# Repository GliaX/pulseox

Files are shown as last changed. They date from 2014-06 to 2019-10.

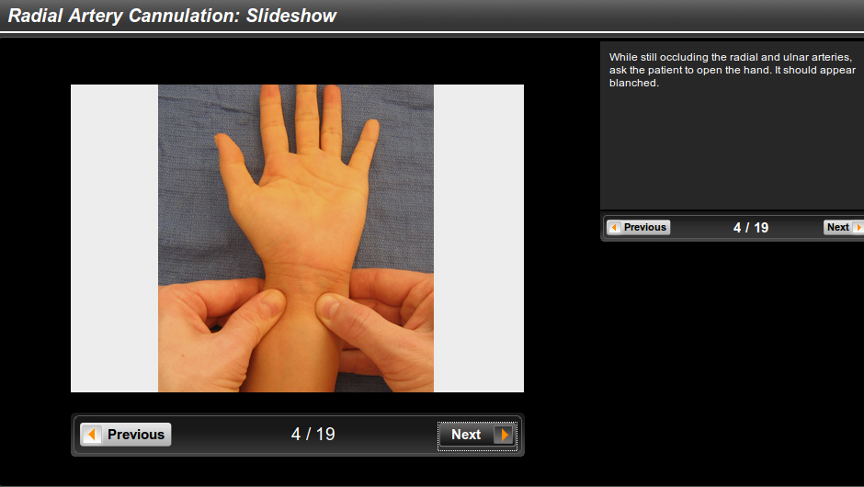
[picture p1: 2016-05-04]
ethics_application/radial_cannulation/radial_explainer_04.png

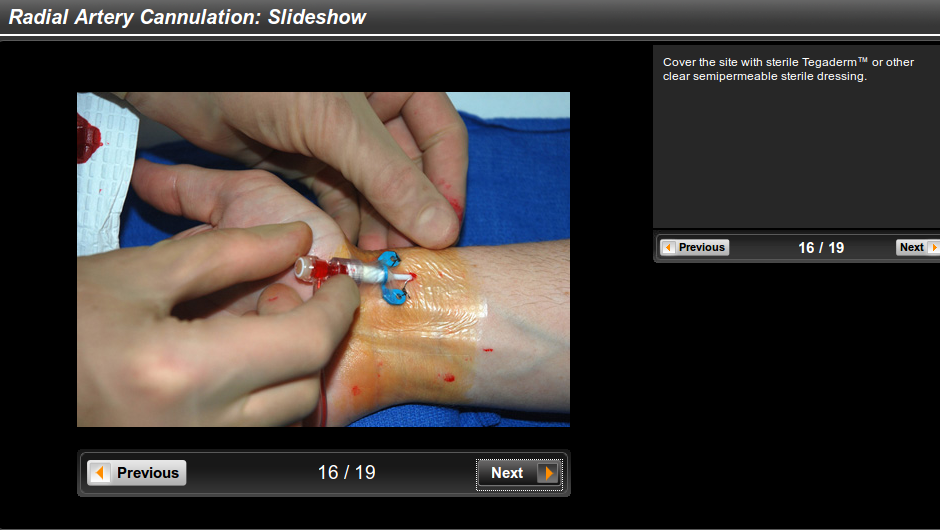
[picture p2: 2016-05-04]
ethics_application/radial_cannulation/radial_explainer_16.png

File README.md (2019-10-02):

Pulse Oximeter
==============

This project aims to create a research-validated pulse oximeter whose plans are available freely and openly. The goal is for the device to cost under USD$25 to produce.

Currently, **THE PULSE OXIMETER IS NOT USABLE AND SHOULD NOT BE USED IN A CLINICAL SETTING.** The current version can be used for laboratory testing only.

Status
======
The device is undergoing clinical calibration as of 2019 OCTOBER 2.

Installation
============
Clone the repository and then do the following to initialize the submodules:

```
git submodule init
git submodule update
```

Licensing notes
===============
As per our understanding, hardware is not covered by copyright. However, we present
our work under the TAPR OHL license insofar as it applies. All software is covered by the GNU aGPL V3

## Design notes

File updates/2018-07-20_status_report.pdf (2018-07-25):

## GliaX Status Report

Progress report since Mon 9. 7. 2018 up to Fri 20. 7. 2018.

PULSE OXIMETER

Features added:
1. finger presence detection implementation
2. automatic LED brightness adjustment algorithm implemented

### 1. FINGER PRESENCE DETECTION

Finger presence algorithm serves both as a user experience feature as well as trigger for other actions, loops and processes that happen in firmware. It takes the level of raw_red signal as a reference to detect the finger presence. As soon as detected level falls below the specified threshold, that means the finger was inserted and device calibration is initialized. Before that, the device is at standby and “FINGER OUT” sign is seen on the display. If the finger is removed during measurement, the device displays the same sign however the brightness level remains the same once the finger is re-inserted and the measurement reappears in a few seconds again.

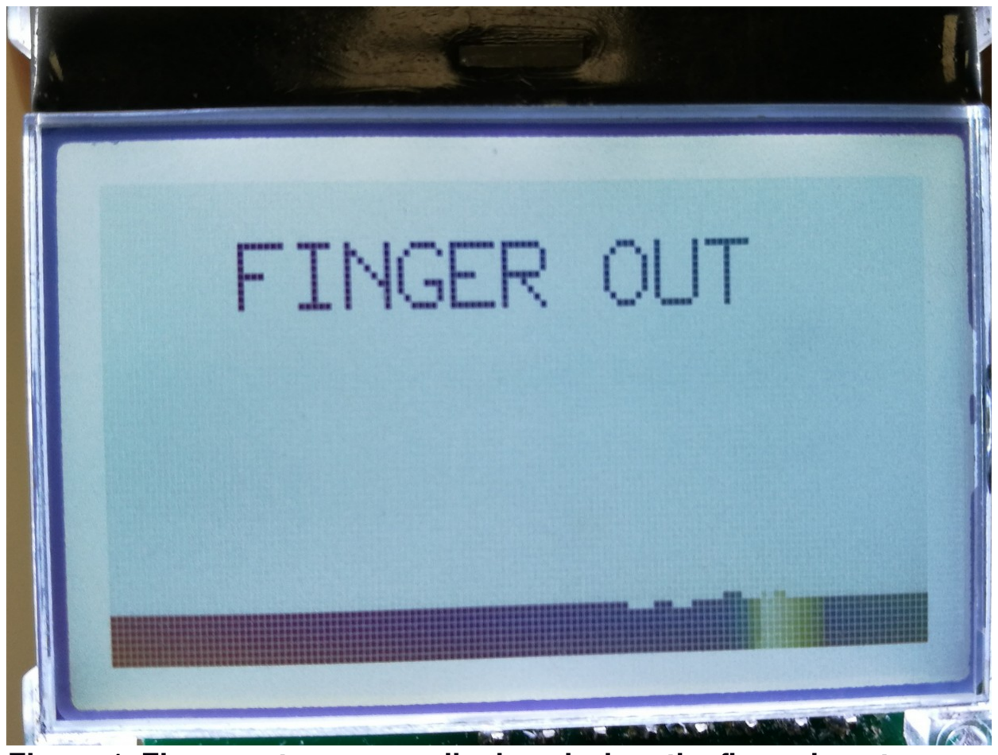
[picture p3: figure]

Figure 1: Finger out message displayed when the finger is not present.

### 2. AUTOMATIC LED BRIGHTNESS ADJUSTMENT ALGORITHM

Device Calibration

Automatic LED brightness algorithm is necessary to compensate for finger light absorption. Light absorption at different wavelengths varies with skin thickness, pigmentation etc. of the person therefore each specimen will have a different optimal light intensity necessary to have the finger illuminated at the right intensity to get the optimal reading.

The calibration process is divided up into setup loop and test loop. The setup loop is initiated right after the finger presence is detected. When pulse is detected, a test loop is initiated which runs the fine optimization. The user sees a message “CALIBRATING...” displayed on the screen¹
until brightness
levels of IR and RED LEDs are successfully adjusted. Afterwards, the device switches to normal operational mode.

1 NOTE: The function for message display is already implemented in the firmware but is not yet turned on due to chip memory issues. The code will first be optimized to increase available ROM, then the function will be enabled. Visually it is similar to what is shown in the Figure Figure.

### 2.1 SETUP LOOP

Setup loop is initiated upon the presence of the finger. It begins at initial brightness level²
and changes it
stepwise until pulse is detected. Brightness level change is executed in a fixed time window of 3 seconds, ensuring enough time for detection of at least 2 heart beats when brightness is close to satisfactory level. Once heart beat is detected, the setup loop is terminated and test loop starts instantaneously. This change is still unseen to the user.

2 NOTE: The initial brightness levels need to be tested locally to achieve the time-optimized solution. The current solution will work best with light-skinned people, but could take a little more time to settle when used on a patient with more pigment.

### 2.2 TEST LOOP

The test loop starts as soon as heart beat is detected and is there to achieve the best signal-to-noise ratio after we already have a useful signal. It is based upon an invented variable that describes ratio between noise and useful signal in the measurement. The variable is named Signal Quality Index (SQI) and is calculated as

SQI = 1 STD/AMP – | (1)

where STD is the signal standard deviation of the signal noise and AMP is signal amplitude when noise is filtered out (see Block diagram in the Figure 2).

Upon successful stabilization of IR and RED brightness levels, the device switches into normal operating mode. At this point the best possible signal quality is achieved.

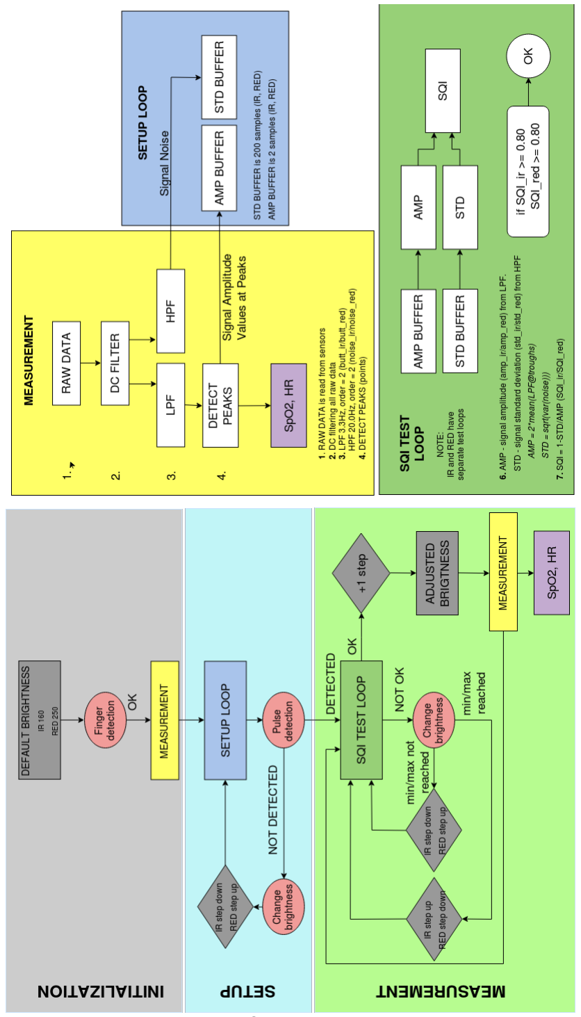
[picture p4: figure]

Figure 2: Code block diagram.

Safety Measures

AVOIDING CONTINUOUS CALCULATIONS
To avoid continuous calculations, we first check for presence of finger in the sensor, and only then brightness adjustment function starts. Brightness adjustment is happening in predefined steps (which can be adjusted) between max and min possible value (also predefined). To make sure the process takes the least possible time, we change brightness in both directions, up and down. This way we ensure that we reach optimal brightness as soon as possible.

REMOVAL OF FALSE-POSITIVES IN PEAK DETECTION
When detecting a pulse from signal peaks, we need to avoid detecting false positives. For that purpose a threshold value was empirically derived and introduced as a safety parameter.

BUFFER MANAGEMENT
When calculating SQI values we need to ensure that all data used is time-aligned. This is done by emptying all used buffers after each test loop iteration. The test loop runs on IR and RED signal completely separately.

VALUE THRESHOLDS
Signal minimum and maximum threshold values were introduced ensuring that too noisy or too weak signals are ignored.

Next Steps

- retesting of the automatic brightness adjustment algorithm
- Finalization of project documentation
- Release debug version of firmware to Tarek Loubani for testing

To be completed by: 27. 7. 2018

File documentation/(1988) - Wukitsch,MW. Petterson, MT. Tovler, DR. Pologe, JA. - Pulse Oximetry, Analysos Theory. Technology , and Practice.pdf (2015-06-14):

# Knowing Your Monitoring Equipment

PULSE OXIMETRY: ANALYSIS OF THEORY,

## TECHNOLO6Y, AND PRACTICE

Michael W. Wukitsch, BA,
Michael T. Petterson, BA, RRT, CPFT, David R. Tobler, BSEE,

### and Jonas A. Pologe, BSEE

Wukitsch MW, Petterson MT, Tobler DR, Pologe JA. Pulse oximetry: analysis of theory, technology, and practice.
J Clin Monit 1988;4:290-301 ABSTRACT, Interest in two-wavelength classic, that is, nonpulse, oximetry began early in the 20th century. Noninvasive in vivo measurements of oxygen saturation showed promise, but the methods were beset by several problems. The pulse oximetry technique, by focusing on the pulsatile arterial component, neatly circumvented many of the problems of the classic nonpulse arterial approach. Today's pulse oximeter owes a good measure of its success to the technologic advances in light emission and detection and the ready availability of microcomputers and their software. Many clinicians have recognized how valuable the assessment of the patient's oxygenation in real time can be. This appreciation has propelled the use of pulse oximeters into many clinical fields, as well as nonclinical fields such as sports training and aviation. Understanding how and what pulse oximetry measures, how pulse oximetry data compare with data derived from laboratory analysis, and how the pulse oximeter responds to dyshemoglobins, dyes, and other interfering conditions must be understood for the correct application and interpretation of this revolutionary monitor.
KEY WORDS. Measurement techniques: pulse oximetry. Monitoring: oxygen. Equipment: pulse oximeters.

THE THEORY

From Ohmeda, 1315 W Century Dr, Louisville, CO 80027. Address correspondence to Mr Petterson.

I placed my prism at this [light] entrance, that it might be refracted to the opposite wall. It was at first a pleasing divertissement to view the vivid and intense cotours produced thereby... [Sir Isaac Newton (1642 to 1727), in a report in the Philosophical Transactions for 1672]

Light was, therefore, recognized to contain all colors of the visible spectrum of electromagnetic energy. Measurements of electromagnetic vibrations are frequency, expressed in hertz (Hz) (1 Hz = one cycle per second) and wavelength, expressed in nanometers (nm) (1 nm = one thousand millionth [1 x 10 -9] of 1 m). Red light, as used in PuLs~ OXIMETRY, can be measured at a frequency of 4.3 x 1014 Hz or a wavelength of 660 nm. The nanometer, yielding numbers much easier to deal with, is the unit typically used when discussing this part of the spectrum.
Newton's theory fostered the techniques of spectral analysis--that is, the ability to detect elemental composition by defining the unique light absorption "fingerprints." A major theoretic statement in early laboratory spectral analysis was the Beer-Lambert (or Bouguet's) law. Simply, this law states that the concentration of absorbant in solution can be determined as a mathematical function of the amount of light transmitted through the solution, providing that the intensity of incident light, the path length, and the ~XTINCTION CO-

290 Copyright © 1988 by Little, Brown and Company

Monitoring Equipment: Wukitsch et ah Pulse Oximetry 291

,=,
I eeOnm

o

X
LtJ

-2
6oc

(l~=~,=mo)
94Ohm
\
\ | \

Hb

I, | t, | I | t | ! | l
700 | | aoo | | aoo | looo
WAVELEENGTH (nm)

Fig 1. Oxyhemoglobin (HbO2) and reduced hemoglobin (Hb) exhibit markedly different absorption (extinction) characteristics relative to red light at 660 nm and infrared light at 940 nm. (Courtesy of Ohmeda)

EFFICIENT of a substance at a particular wavelength are known. The absorbance of light by HEMOGLOBIN (Hb) and oxyhemoglobin (HbO2) as a function of wavelength is shown in Figure 1. The absorbance or, more correctly, extinction of HbO2 at the red wavelengths (650 to 750 nm) is less than that for Hb. Hence, HbO2 is more transparent to red light than Hb is. Figure 1 also shows that the reverse is true, to a lesser degree, in the infrared region (900 to 1,000 nm). Research led by Nicolai, Kramer, Elam, Matthes, Millikan, and Wood in the early to mid-1900s sought ways to apply these facts to determine the HbO2 concentration, or arterial blood oxygen saturation (SaO2) [1].
Complex and numerous problems of applying the Beer-Lambert law to in vivo analysis brought the development of two-wavelength, in vivo oximetry to a halt during the 1950s. Why the Beer-Lambert law was not totally effective becomes apparent when we examine how light behaves in this application.
As the law of conservation of energy states, energy cannot be "created or destroyed"--and this applies to light energy. For the Beer-Lambert law to work, all light in the system should be accounted for, that is, incident light = light transmitted + light absorbed. This can work in a very controlled experiment with relatively short path lengths. Experiments with human tissue present several obstacles. Consider: incident light = light transmitted + light absorbed + light scattered + light reflected. On human subjects:
- Light is scattered by the skin surface, tissue, muscle, bone, and blood.

* Light is reflected by the skin surface, which can be a function of skin surface texture and color.
- Light is absorbed by tissue components other than the blood and absorption is also dependent on pigmentation and thickness of the test site.
- The blood is a nonhomogeneous liquid capable of nonlinear absorption of light, particularly as hematocrit varies.

The CLASSIC OXIMETRY (that is, nonpulse, two-wavelength, in vivo oximetry) could not deal effectively with all the variables.

EVOLUTION OF PULSE OXIMETRY

The prominent forerunner to the pulse oximeter was the Hewlett-Packard ear oximeter (HP 47201A), which used a tour de force of technology to solve the problems found in the two-wavelength approach. By using eight wavelengths (from 650 to 1,050 nm), this unit compensated for all the effects of "skin pigmentation, ear thickness, or earprobe motion" [2]. Featuring precalibration, ear vascularization via heat, and a fixed path length, this unit solved many of the problems that plagued earlier devices [31.
Clinical accuracy tests pointed to the ear oximeter as an acceptable device that was a boon to the puImonologists and sleep researchers of the mid-1970s. Although it was thought to be the "gold standard" for oximeters, recent tests at low saturations uncovered unstable performance below an arterial oxygen saturation (SaO2) of 70%, and its inability to deal with carboxyhemoglobin (HbCO) is documented [4,5].
A major advance came with the recognition that the pulsatile nature of the arterial blood can be exploited in oximetry. Pulse oximetry uses the physiologic activity of the cardiac pulse as the basis for a system to determine SaO2. The idea of using the cardiac rhythm as a "filter" for in vivo measurement was first attempted in Japan. This new concept took commercial form in the Mochida Oximet (eventually Minolta), the first pulse oximeter manufactured and marketed. This unit relied on analog electrical circuitry and had bulky fiberoptic cables similar to those of the Hewlett-Packard ear oximeter. Its performance was nearly acceptable clinically, with marginal accuracy, "_+ 5% of that obtained from the blood gas method" [6], and it exhibited some problems with artifacts: "The measurement is interrupted when the fingertip changes its position against the light beam. This frequently occurs when the patient is shivering" [6]. As with classic oximetry, early pulse oximetry had to contend with limitations inherent in the hardware.

292 Journal of Clinical Monitoring Vol 4 No 4 October 1988

10

0

0
o
c-O
0 .1

×
ILl

.01
600
Log~
~ | methemoglobin

~ogtobm

carboxyhemoglobin
I | I | I | I | I | 1 | ~ | | I | I
640 | 680 | 720 | 760 | 800 | 840 | 880 | 920 | 960 | 1000
Wavelength (nm)

Fig 2. Hemoglobin extinction curves showing relationship of reduced hemoglobin, oxyhemoglobin, carboxyhemoglobin, and methemoglobin to light absorption. (Courtesy of Ohmeda)

The first successful new-breed pulse oximeter, the Biox II (Ohmeda), ushered in a new era. The Biox II was a microprocessor-based, convenient-to-use, smaller, and less expensive device having clinically acceptable accuracy [7, 8]. Major interest in pulse oximetry in the United States was sparked by the efforts of Dr William New (Nellcor), who saw the advantage of oxygenation monitoring during anesthesia. Optimizing one of the key elements of this new approach--small, inexpensive light emitters and detectors--the Nellcor N100 featured disposable sensors.

PULSE OXlMETRY: PRINCIPLES

In order for spectrophotometric measurements of blood to be made in vivo a number of criteria must be met:

1. The tissue must be reasonably transparent to the wavelengths of light that are to be considered for the measurement.
2. The absorption characteristics must be different between the specific species for each wavelength that is to be considered.
3. There must be a reasonable method for producing the wavelengths that are being considered.
4. There must be an acceptable means of detecting the wavelengths of interest.
5. The minimum number of discrete wavelengths that are required must be equal to the number of significant absorbers that are present.

The first criterion limits the range of wavelengths that are reasonable choices to the red and near-infrared regions. Tissue and pigmentation absorb the blues, greens, and yellows, and water absorbs the longer infrared wavelength. As can be seen in Figure 1, Hb and HbO2 vary substantially relative to each other in the 600- to 1,000-nm range (red to near inffared)--this meets the second criterion. The availability of light sources in this region is quite good. There are a variety of light-emitting diodes (LEDs) with outputs in this wavelength region; they are commonly used for displays and optical communication applications. In addition, they are small, efficient, and reasonably stable. Two common LEDs have nominal wavelengths of 660 and 940 nm. The wavelengths in the range of 600 to 1,000 nm are also easy to detect v¢ith a silicon photodiode, thus fulfilling the fourth criterion. The last criterion is less straightforward. Obviously there are absorbers other than Hb and HbO2 in the blood. (Figure 2 shows the absorption characteristics of methemoglobin [MetHb], HbO2, reduced Hb, and HbCO.) Fortunately these four types of lib are the only significant absorbers normally found in blood. Note that at 660 nm, the MetHb and the Hb have similar extinctions (a measure of absorption), as do HbCO and HbO2. If only two

Monitoring Equipment: Wukitsch et al: Pulse Oximetry 293

TIME

Variable absorption due to pulseadded volume of arterial blood Absorption due to arterial blood Absorption due to venous blood

Absorption due to tissue

Fig 3. Tissue composite shows dynamic and static components affecting light absorption. (Courtesy of Ohmeda)

wavelengths are used the effect is, very roughly, to "lump" or combine MetHb with Hb and HbCO with HbO2.
The MetHb being seen as Hb usually is not clinically significant; because it is not carrying oxygen the oxygen saturation value is still correct. HbCO does present a problem because it will be "counted" as an oxygencarrying form and thus cause the measured oxygen saturation value to be reported larger than it actually is. The effects of these and other absorbers, such as dyes, are discussed later.
For a workable system, the signals coming from arterial blood must be isolated from those representing venous blood, tissue, and other absorbing material. The method by which this is accomplished is responsible for the termpulse oximetry. Figure 3 represents a tissue cross section. Note that light absorption by the various substances is constant over time, with the notable exception

Fig 4. Graphic representation of compensation process that must occur before light intensities at two wavelengths can be used for calculation of arterial oxygen saturation. This scaling process can be accomplished by several methods, electrically or mathematically,
AC = alternating current; DC = direct current; IR = infrared. (Courtesy of Ohmeda)

of arterial blood. The absorption signals from arterial blood vary with each contraction of the heart as the volume of arterial blood changes.
It is convenient to define the varying or dynamic part of the signal as the alternating current (AC) signal and the static component as the direct current (DC) signal. The amplitude of the DC signal is affected by the intensity of the light source, sensitivity of the detector, and amount of constant absorbers that are present (sample thickness). These same factors will affect the AC signal amplitude, as will the perfusion (amount of blood volume change per pulse) and the oxygen saturation. To make any useful comparisons between the absorption as the red wavelength and the infrared wavelength the AC signals must be scaled by the DC signals. Dividing the AC level by the DC level (at each wavelength) gives a corrected or scaled AC level that is no longer a function of the incident intensity [9].
This scaling process, performed by electronics, mathematics, or otherwise, yields values that are compensated for variations in incident light intensity and represent the relative absorption of light at two wavelengths that is due to only the hemoglobin in the arterial blood (see Fig 4). The numeric ratio of the corrected red value to that of the corrected infrared value yields a result that is easily converted to oxygen saturation, as shown in Figure 5. Figure 6 shows what the relative red and inflared AC signals would look like for various saturations.
The pulse oximeter's focus on just the "dynamic" arterial flow, along with the compensation process, neatly circumvent nearly all of the obstacles that have plagued the classic oximetry technique. Like all elegant solutions, pulse oximetry uses a simple concept to defeat complex problems. The simplicity, however, is deceptive.

AC--

~RAW ~ SIGNAL LEVELS
{WITH DC LEVELS UNEQUAL}

## Do ili ii ii!i!iiiiii'i' :ili iiiiiii

=SCALED ~ SIGNAL LEVELS
(WITH DC LEVELS EQUAL}

100
90
80
70
60
o ~ 50

40

30

20
10

0

Fig 5. Relationship of red (R)/infrared (IR) numeric ratio value to arterial oxygen saturation (SaO2).

PULSE OXlMETRY: PRACTICE

Converting the principles just described into a practical device for clinical application involves many additional considerations. These include technical issues related to optics, signal-to-noise ratios, data acquisition, signal processing, mechanical configuration, and human interface.
The oximeter probe consists of light sources (LEDs), a detector (photodiode), and an appropriate mounting structure to support the specific method of application. Electronically, the probe is quite simple in that the only necessary function is the ability to turn the LEDs on and off and to provide for the detected signal to be returned to the main electronics for processing. In addition, the probe provides a means of identifying itself to the system for calibration purposes. The mechanical structure today (owing much flexibility to the ideal light emitters and detectors that are available) is optimized on the basis of the intended application.
Electronically, the pulse oximeter consists of the following:
1. LED timing and probe control
2. Analog signal conditioning and/or processing
3. Data acquisition
4. Digital signal conditioning and/or processing
5. Display and control system
6. Internal system diagnostic functions

Three different light levels are measured by the detector: the red light level, the infrared light level, and the ambient light level. To accomplish this with a single detec-

O~

85~

100~

660nm (RED)

0 | 0 | 0 | 0 | 0 | 0 | 0 | 0 | 0 | 0 | 0 | 0 | 0 | 0 | 0 | 0
0 | C) | 0 | 0 | 0 | 0 | 0 | 0 | 0 | 0 | 0 | 0 | 0 | 0 | 0 | 0
6 6 6 ,.: ,; ,/. ,.: ,: ei gl 14 gl i4 ~4 ,,i ,4 8___
IR

940nm (IR)

/%_ ==3.4

1.0

- 43

Fig 6. Relative plethysmographic signal amplitudes and arterial oxygen saturation (SAG2) values assuming the transmission intensities are equal. R = red; IR ---- infrared.

Fig 7. Ohmeda light-emitting diode timing sequence shows frequency and first step of ambient light filtration process. R = red; IR = infrared; DC -- direct current. From Wukitsch MW. Pulse Oximetry: Historical Review and Ohmeda Functional Analysis. International Journal of Clinical Monitoring and Computing, Vol 4, pp 161-166, 1987. Used with permission.

tor the light sources must be sequenced on and off. Figure 7 shows the light timing sequence used in the Ohmeda 3700 oximeter. Each time the red LED is on, the analog electronics obtain a sample of the red intensity. This occurs likewise for the infrared LED. By measuring the light tevel when both LEDs are off, it is possible to subtract this level from each channel (red and infrared) on an instant-by-instant basis. This serves to compensate for ambient, or room, lighting, which may

Monitoring Equipment: Wukitsch et at: Pulse Oximet~ y 295

A

Fig 8. Representation of light-emitting diode sequencing occurring over 1/3o of 1 second as it relates to red (R)-infrared (IR) intensity sampling and the instantaneous arterial oxygen saturation (SaO2) calculation and the second step qsC ambient light filtering. To = time zero, or "'start"; T1 = time one, or "finish." From Wukitsch MW. Pulse Oximetry: Historical Review and Ohmeda Functional Analysis. International Journal of Clinical Monitoring and Computing, l/ol 4, pp 161-166, 1987. Used with permission.

change during the course of routine monitoring. Sequencing the LEDs at a frequency that is an integer multiple of the power line frequency allows the system to operate "synchronously" with "flickering" room lights (fluorescent lights normally generate a 120-Hz flicker on 60-Hz power). This avoids light flickerinduced fluctuations on the probe's photodetector, which could distort or disguise the tiny signals representing actual arterial blood flow'.
The light timing sequence, shown in Figure 7, cycles at 480 times per second (60-Hz power). A "stream" of these sequences, as depicted in Figure 8, shows the timing as it relates to the INSTANTANEOUS ARTERIAL OXYGEN
SATURATION (SaO2i) CALCULATION, which occurs thirty
times per second (60-Hz power):* It is significant that the 480-Hz timing, 60-Hz power, and 30-Hz SaO2i calculation are numerically related. The timing and sequencing frequencies serve as a filter against environmentally induced error [10].
Why SaO2i at 30 times per second? Since the pulse oximeter is making use ofpulsatile flow signal, the simplest approach might be to measure the minimum to maximum value (delta [A]) at the red and infrared wavelengths for each pulse and use this A red/A infrared value to calculate gaO 2 (Fig 9A). This method works but has a

*The light timing sequence and SaO2i calculation occur at 480 and 30 Hz, respectively, with 60-Hz power. With 50-Hz power, these numbers are 400 and 25 Hz, respectively.

B

Fig 9, Changes in light intensity can be measured at the minima and maxima points of the pulse wave or many times along the wave. X-X produces a change in intensities (A) on both red and infrared wavelengths. (A ) represents the change in light intensity from the minima to the maxima point on the arterial pressure wave form from which saturation can be calculated once per heart beat. The multiple measurements depicted in (]3) allow many sample points that can be subject to validation schemes such as the running weighted average. (Courtesy of Ohmeda)

number of unacceptable side effects. The first is that a calculation of oxygen saturation is possible only once per heart beat. Because some method of averaging the saturation values is required to minimize the effects of artifacts, and because there is a clinical requirement that the response time to changes in saturation be reasonably fast, one measurement per beat allows no more than ten measurements to be averaged for the system to maintain an acceptably short response time (10 s at 60 beats/ min). However, it is possible to make use of the principle that the sum of the parts equals the whole. By calculating the A, or change, in the signals 30 times per second, we can calculate the SaO2i value regardless of pulse rate (Fig 9B). With this method the Ohmeda pulse oximeter provides 180 saturation values in a 6-second interval (90 values in a 3-second interval). Having this large number of data points allows the use of a comprehensive scheme to selectively "weight" each sample to further enhance the stability of the calculation while maintaining acceptable responsiveness.

Table 1. Simplified Representation of Ten Sa02i Values with Assigned Weights
Variable | At One-Third of 1 Second
SaO2i (%) | 94 | 93 | 94 | 95 | 72 | 30 | 45 | 85 | 95 | 94
wti | 10 | 10 | 10 | 9 | 5 | 1 | 1 | 7 | 9 | 10
SaO2i x wti | 940 | 930 | 940 | 855 | 360 | 30 | 45 | 595 | 855 | 940

Table 2. Displayed Arterial Oxygen Saturation Values Derived from Averaging of Processed Average Values over Three Seconds
| Second 1 | | | Second 2 | | | Second 3
Processed average (avg v) | 92 | 93 | 93 | 92 | 93 | 94 | 93 | 94 | 94 | 90
Displayed Value 1 = 93.1 ~ .Displayed Value 2 = 92.8 a

~The Ohmeda Biox pulse oximeters round decimals up or down.

Analysis of the SaO2i values showed that several factors identify the validity of an individual SaO2i value. These include the magnitude of the A of AC signal for the sample, the point in the cardiac cycle where the data were taken, and the correlation of the SaO2i value with the current displayed "average" saturation value. For example, if SaO2i = 72% and the present 3-second average is 93%, this instantaneous value would be assigned a comparatively low weight. The following example shows a simplification of the processing that uses the WEIGHTED AVERAGING scheme. We assume here a 3-second processing time. Data points taken at 1/30-second intervals are first "weighted" and then "averaged." This produces what we will call a "PROCESSED" AVERAGE (avg v) every 0.33 seconds. Each avg p value is again averaged with the previous eight avg e values, yielding a new SaO2 value that is sent to update the displayed SaO2--in the 3-second mode, every 0.33 seconds.
Table I is a simplified representation of ten SaOai values with assigned INSTANTANEOUS WEIGtITING FAC-TORS (wtis) of 1 tO 10 (1 = lOW value, 10 = high value), indicating SaO2i values over 0.33 second. The wti is based on the perceived validity of the SaO2i value. The following formula is used to determine avgV:
10 | 10
avg p= E(SaO2iJ X "vtiJ)/j~l~rtiJ,
j=l | "=

where j is the number of sample pairs being multiplied. From the values shown in Table 1, we can determine that
10 | 10
2 (SaO2iJ X wti j) = 6, 490 and E wtij = 72.
j=l | j=l

Applying the above formula would yield an avg p value of 90.1 for this 0.33-second period. In the 3-second averaging mode, this avg e (90.1, rounded to 90) is averaged with the previous 2.66 seconds worth of avg e values, producing the new displayed SaO2 values shown in Table 2.
Light transmission measurements during portions of the cardiac cyde showing the greatest A (that is, the rising portion) produce the most valuable SaO2i values. Where the A is small (the flat part of the cardiac cycle, see Fig 9), the SaO2i values call be inaccurate and misleading. It can be seen from the preceding example that, because of this weighted averaging process, the SaO2i values of 72, 30, and 45% have little effect on the total mathematics.
Intuitively, we appreciate that the actual saturation did not change 23% (95 to 72%) in 1/30 second. By using a series of criteria, the microprocessor can assign a value to each instantaneous SaO2 value, thereby placing it appropriately within the system, enhancing both accuracy and stability. The weighted averaging system allows stability over short, sharp aberrations (something like an automobile shock absorber) by filtering out the suspect values. During periods of rapidly changing actual clinical SaO2 values, all "weights" will tend to be reduced, thereby facilitating rapid response and close tracking of patient conditions.

SIGNAL STRENGTH

The signal strength indication can help in judging oximeter function. To return to the AC/DC fraction, our tests have shown that pulsatile strength is adequate when this fraction exceeds 0.2%. (The infrared channel is used in this case as it changes minimally within the normal range of PULSE OXlMETER ARTERIAL OXYGEN SAT-

Monitoring Equipment: Wukitsch et ah Pulse Oximetry 297
iii!iii!iii iN!i iiiiiii iii [,
,: : | | : | | ,,,,,,
: | :: :::: If: :: : : | : :: | 1:: : | /1::: | | | ....... | ,,|.11,.,,|,..
ii!iiii ,, i i-.-:iii! | ....
i ~ : i | i | iiiii~iii!iiii~::., i~iilliN!!ii:, i~iiliiii!"iilk
i i | i | i. | ill| i~i|ill ||ii |i:.. !iNF.'i| ii|i|i|:: . | i:i ||!illii|i!iiii .. i
: | : | :::::::::::::::::::::::::::::::::::::::::::::::::::::::::::::::::::::::::::::::::::::::::::::::
ili!ili!ili ii ii | ..... iw | ii
:!~:'~ • :: ::: :: | ~iiiiiiiiiii: | | K|fii~i~NK .!~mm | | iiN!N!ilh |
!~!!!~|~ | :::, | ii!NiliNi~N:.. | :::::::::::::::::::::: | K-':'N~!iliNII~. | Ii jiiiiiiiii :ii:i .,i | ii,. | i.i,
i:~ "i | i | Nii, i | i~iiiiii~i~:~ | Niiiiiiii~i
:: ::: i~ | 3 | :!NNK|:. | : . | | :=:m:mm | : :nm:=mm | . | .

,
Fig 10. Wave form examples. S = slow response; SGNL = signal strength indicator.

URATION (Sp02) values as compared with the red channel):

(AC/DC) x 100 > 0.2% = adequate pulsatile signal.

On the Ohmeda 3700 oximeter the signal strength indicator (SGNL) registers "full" when the value is 1%. We have chosen to show only this "bottom" 1% area (even though a 3% ratio can be considered normal and 10 to 11% high) because this factor becomes important in the low ranges. A message, "Low-Quality Signal," will be displayed if the signal strength indicator falls below 0.2% (Fig 10). Although SpO2 values may still be valid, we believe clinicians should be warned of this low pulsatile level, which can result, for example, from shock, cold temperature, decreased cardiac function, or low hematocrit.
The system of weighting factors also can influence the signal strength display. Low weights can be assigned to SaO2~ values due to a low AC level or inconsistent SaO2i calculations. When the weighting factors are summed in preparation to calculate the avg P, this total, below a certain number, will also drive the signal strength indicator down. Therefore, the indicator will fall during low AC levels (poor perfusion) or low SaO2i weights (artifact, etc), or both.

Ptethysmographic Wave form
The Ohmeda 3700 pulse oximeter was the first to display a "plethysmographic" waveform, presenting a familiar picture to the clinician. With the plethysmographic waveform, problems related to probe placement or artifact that may not be recognized by the microprocessor and that may not be apparent from other types of displays (for example, amplitude only) can be observed by the clinician and acted on, satisfying the major requisite: that the pulse oximeter has pulsing arterial blood as the source of its signal [11,12].
The plethysmographic waveform display plus the signal strength indicator allows the clinician to use the pulse oximeter under the most difficult circumstances--for instance, vasoconstriction or heart massage--and to assess when displayed oxygenation levels are based on true arterial blood flow or on artifacts by observing the shape of the waves. Clinicians seasoned in the use of the pulse oximeter have used the rule of thumb that the SpO2 value is valid when the oximeter pulse rate and electrocardiographic (ECG) heart rate are within one to two beats of each other. With the waveform display this observation is not necessary. Thus, the waveform display, now available on several models, makes the pulse oximeter a more useful and reliable device--particularly for monitoring the most compromised patients [13].

INTERFERING SUBSTANCES

Dyes
Because pulse oximetry works on the principle of light absorbance, dyes introduced into the blood stream could interfere with the calculation of SaO2. Dyes such as methylene blue, indocyanine green, indigo carmine, and fluorescein have been studied. Their effects range from significant to negligible, respectively [14,15]. Methylene blue has the highest peak absorbance of these dyes at 660 nm, and therefore has the greatest effect on pulse oximetry. The relationship is inversely proportional: the greater the amount of methylene blue, the lower the SpO2 displayed. Of interest is the fact that methylene blue also depresses the readings measured by the CO-OxIMETER. Suffice it to say, the clinician should be aware that these dyes may interfere with light transmission at the red or infrared wavelengths used, causing errors in the displayed pulse oximetry readings.

HbCO and MetHb
Of perhaps greater importance (as previously mentioned) are the effects of HbCO and MetHb on the pulse oximeter. HbCO is a problem of urban life and, of course, is a consequence of smoking. In most nonsmokers, HbCO levels are below 2% but can be higher depending on the local environment [16]. MetHb levels are routinely less than 1%. However, methemoglobinemia does occur, and its effect on pulse oximetry is a source of controversy.
We studied the effects of both HbCO and MetHb on pulse oximetry with an in-house computer simulation. Both HbCO and MetHb tend to elevate the SpO2 value displayed to greater than the actual SaO2. HbCO has a larger effect than MetHb on the displayed number. For example, with an actual SaO2 of 90% and an HbCO level of 10%, the SpO2 value would be approximately 97 to 98%. The effect is less at lower SaO2 values. At an actual SaO2 of 60% and 10% HbCO, the displayed SpO2 value would be approximately 64%. Barker et al
[17] recently demonstrated this effect in a canine model. For MetHb, at an actual SaO2 of 90% and an actual MetHb level of 10%, the SpO2 value would be approximately 91.5%. However, at an SaO2 of 60% and 10% MetHb, the SpO 2 value would be approximately 66.5%. This effect also was demonstrated recently in a canine model [17].
Clinically, the errors produced by HbCO and MetHb usually are not significant. These substances (as long as their concentrations remain relatively constant) have no effect on the pulse oximeter's ability to trend. When the accuracy of pulse oximetry is being tested, subjects or patients with HbCO greater than 3% and MetHb greater than t.5% are best excluded. The calibration of the Ohmeda Biox 3700 was performed on healthy nonsmokers with an average HbCO level of 1.6% and an MetHb level of 0.4% to limit false results.

Fetal Hemoglobin
High levels of bilirubin and fetal hemoglobin (HbF) have always been presented as possible problems for pulse oximetry. Bilirubin was known to have an effect on the Hewlett-Packard ear oximeter [18]. However, the two wavelengths used by current pulse oximeters are, in theory, relatively immune to the influence of bilirubin. A recent clinical report confirms this [19]. It is well known that HbF shifts the oxyhemoglobin dissociation curve to the left. Thus, the question has arisen, is the pulse oximeter (which was calibrated for adult Hb) actually reflecting true SaO2? A theoretical model generated in-house, as well as experimental data recently published [20], demonstrate that HbF has no clinically significant effect on pulse oximetry. The degree of HbF of course affects the correlation of SaO2 to arterial oxygen tension (PaO2). Clinicians concerned with the PaO2 value must have an understanding of the HbF level when interpreting the SpO2 reading.

ACCURACY

Pulse oximeters are adjusted for accuracy by the use of empirically observed data from human subjects. Early testing showed that this technique produced a clinically acceptable device [21]. However, in a recent interbrand comparison, the ~actual level of pulse oximeter accuracy "differed widely between instruments" [22], even though manufacturers specify the same relative accuracy.
In vivo experiments make available data in the region of 80 to 100% SaO2, enabling manufacturers to ensure good predictability in this range. It is typically difficult to get sufficient numbers in the 60 to 75% SaO2 range to ensure accuracy within this range, thus manufacturers are forced to extrapolate their 80 to 100% results downward. This fact caused some surprises and a few red faces when Severinghaus and Naifeh [22] gave manufacturers accuracy test results at the 50% SaO2 level. Accuracy at 50% SaO2 initially was not consistent among the models tested. Whether accuracy at 50% SpO2 is required is arguable, as clinicians generally strive to keep patients at SaO2 levels above 90%. Nevertheless, manufacturers seized this opportunity to improve performance in the low ranges.
The question of pulse oximeter accuracy, particularly at or near the limits of its capabilities, still surfaces occasionally. Pulse oximeter performance has been well studied; a computer search of the literature on pulse oximetry recently turned up nearly 150 titles dealing with accuracy (from a total of more than 500 articles). These reported tests show that:

Monitoring Equipment: Wukitsch et al: Pulse Oximetry 299

1. Accuracy results show fair consistency.
2. Test conditions vary, as does the subject population.
3. Pulse oximeters are compared with (a) SaO2 calculated from blood oxygen tension, [SaO2 (CALC)];
(b) SaO2 determined spectrophotometrically by a CO-Oximeter [HbO2 or SaO2 (FRAC)]; and (c) other noninvasive oximeters.
4. Performance is acceptable for most dinical settings.
5. Accuracy results many times fall outside of manufacturers' specifications.

It should be noted that past reports suggesting that the pulse oximeter measures "FUNCTIONAL" ARTERIAL OXY-GEN SATURATION [SaO 2 (FUNC)] appear to have been recently disproven [17].
Most researchers understand that the device best suited for establishing pulse oximeter accuracy--a standard, if you will--is the CO-Oximeter.
Typically, these spectrophotometric devices determine HbO2, HbCO, and MetHb. Although the CO-Oximeter value may not equal an SpO2 value, an understanding of the HbCO and MetHb components can assist in the interpretation of the SpO2 value.
SaO2 calculated from arterial oxygen tension [SaO 2 (calc)] may be different from actual SaO2. In order to calculate SaO2 from arterial oxygen tension, correction factors for temperature, arterial carbon dioxide tension (PaCO2), 2,3-diphosphoglycerate, and hematocrit must be inserted. Most often, arterial blood gases (ABGs) are analyzed with standard correction factors; seldom are all variables measured and inserted into the calculation. These factors can alter the shape and position of the oxyhemoglobin dissociation curve and, therefore, the derived SaO 2. SaO 2 (calc) from ABG is also "blind" to HbCO, although for a different reason and to a different degree than the pulse oximeter. The most appropriate "standard" to use as a gauge to pulse oximeter performance, then, is the CO-Oximeter [23]. Statistical analysis provides the tools necessary to compare the SpO 2 value to the "standard" of laboratory-derived results. When properly used, the various calculations, such as standard deviation, regression line, and standard error of estimate, can lead to an exact understanding of the data. These analytic devices plus an understanding or selective screening of the subject population can lead to a tightly controlled assessment of performance that is of fundamental importance to both the clinician and the manufacturer. Expecting that resuits of a meticulously controlled study will be viable in everyday clinical usage can be misleading, however. Extensive use of pulse oximetry over a wide range of situations and conditions has shown that readings can vary over a relatively wide band--Certainly beyond the manufacturers' specifications. The problems of small signal, susceptibility to artifact, skin and tissue factors, patency of arterial flow', venous pulsations, and dyshemoglobins in combination can contribute to SpO2 inaccuracies approaching five or more percentage points from true SaO 2.
The terms tolerance interval and prediction limits are useful in qualifying the pulse oximetry reading. These represent boundaries within which the pulse oximeter is correctly indicating, as a function of time: "It appears that, . . . the 99% prediction limits are within -+ 8% of the calculated regression line" [24]. This means that the pulse oximeter reading is within 8% of actual SaO2 99% of the time (assuming the calculated regression line equals the line of identity). Lowering or tightening the variation also lowers the confidence (that is, +--95% prediction hmit within -4%). The tolerance interval [25] and prediction limit both are useful. For example, with a 99% prediction limit of -+ 8%, when SaO2 is 90%, SpO2 will be 82 to 98% 99% of the time; with a 95% tolerance interval of -4.5 to + 5.5, when SaO2 is 90%, SpO2 will be 85.5 to 95.5% 95% of the time.
Even though many factors can affect the accuracy of the SpO2 reading, the pulse oximeter's value is its ability to provide precise--if not 100% accurate--oxygenation data on a continuous basis. Several recommendations can be made to increase the likelihood that SpO2 readings will be within or close to manufacturers' specifications:
First, patient probes must be used according to manufacturers' recommendations. Second, the pulse oximeter must be "focused" on pulsing, arterial blood. A pulsatile display is mandatory; a display that show's the arterial waveform is best. Third, an acceptable signal size or strength must be verified (adequate perfusion). Fourth, it is advantageous to observe close correlation between pulse rate (pulse oximeter) and heart rate (ECG), particularly with nonwaveform oximeters. (This gauge of quality control, unfortunately, is lost when the ECG heart rate takes the place of pulse rate on oximeters relying on ECG for validity,)
Although the "standard" for pulse oximeter accuracy is somewhat nebulous, the weight of the literature points to acceptable clinical performance in a wide and growing variety of applications.

SUMMARY

In pulse oximetry, we have technology that is simple to understand--deceptively simple. The concepts involving light absorption are straightforward. The use of pulsing arterial blood as a first-line filter is clear. At first glance, the oximeter appears to be no great problem to design or, for that matter, to use. Years of experience have taught us that this is not the case. Producing a device that works on all patients and in all clinical circumstances has taxed the technologic capabilities of device manufacturers. The investment necessary for a proper range of patient probes, for instance, is extremely high. Pressure for increased performance has all manufacturers searching for improvements in function, features, and hardware and software in the attempt to satisfy all the clinical requirements. These demands have led to added complexity, not only in the equipment, but also as concerns the users' appreciation and interpretation of the pulse oximeter measurement. As with all patient monitors the value of the pulse oximeter must be properly interpreted for a given patient.
Ultimately, the value of oxygenation data, the relative ease of use of the pulse oximeter, and the impact this device has made on clinical practice combine to justify the claim that pulse oximetry is the most important new monitor of this era.

The authors thank Di Schenk for word processing and R. Hall and M. Hibl for artistic support.

GLOSSARY

CLASSIC OXIMETRY Multiwavelength noninvasive oximetry that does not use the cardiac cycle (that is, arterial pulsations) as the basis for its calculation of arterial oxygen saturation.
CO-OxIMETER A laboratory device that spectrophotometrically measures hemoglobin, oxyhemoglobin, carboxyhemoglobin, and methemoglobin. EXTINCTION COEFFICIENT a numeric measure of opaqueness; the greater the number, the greater the opaqueness. Hb In this text often used to express reduced hemoglobin or hemoglobin unbound to oxygen.

INSTANTANEOUS ARTERIAL OXYGEN SATURATION CAL-
CULATION | See SaO2i.
INSTANTANEOUS WEIGHTING FACTOR (Wti) | A weighting
factor assigned to each INSTANTANEOUS ARTERIAL OXY-GEN SATURATION value in the Ohmeda Biox pulse oximetry system.
PROCESSED AVERAGE (Avg P) The pulse oximeter arterial oxygen saturation value derived from the sum of the
product of the INSTANTANEOUS ARTERIAL OXYGEN SAT-URATION and the INSTANTANEOUS WEIGHTING FACTOR di-
vided by the sum of the weighting factors on Ohmeda pulse oximeters.

PULSE OXIMETER ARTERIAL OXYGEN SATURATION See SpO2.
PULSE OXIMETRY Two-wavelength noninvasive oximetry that uses the cardiac cycle, that is, arterial pulsations, as the basis for its calculation of arterial oxygen saturation.

FUNCTIONAL ARTERIAL OXYGEN SATURATION See SaO2
(func).
SaG2 (calc) Arterial oxygen saturation calculated from pH and arterial oxygen tension at 37°C according to a standard dissociation curve.
SaO2 (frac) Arterial oxygen saturation measured spectrophotometrically by a CO-Oximeter: HbO2/(HbO2 + Hb + MetHb + HbCO) x 100.
SaO2 (func) Arterial oxygen saturation calculated from measurements of variables derived from a CO-Oximeter: %HBO2/100% - (%HbCO + %MetHb) × 100.
SaOzi Value of arterial oxygen saturation derived every 1/30 second by Ohmeda Biox pulse oximeters. SpO2 Arterial oxygen saturation as measured by pulse oximetry.
WEIGHTED AVERAGE The sum of a number of PROCESSED AVERAGES divided by that number, which yields the displayed arterial oxygen saturation value on Ohmeda Biox pulse oximeters. (The number may be 9, 18, or 36, depending on which operating mode is selected [fast, normal, or slow]).

REPERENCES

1. SeveringhausJW, Astrup PB. History of blood gas analysis. J Clin Monit 1986;2:174-189
2. Merrick EB, Hayes, TJ. Continuous noninvasive measurement of arterial blood oxygen levels. Waltham, MA: Hewlett-Packard, 1976
3. Saunders NA, Powles ACP, Rebuck AS. Ear oximetry: accuracy and practicability in the assessment of arterial oxygenation. Am Rev Respir Dis 1976;114:745-748.
4. Cissick JH, Yockey CC, Byrd RD. Evaluation of the Hewlett-Packard ear oximeter for use during routine air transport of patients. Aviat Space Environ Med 1981; May:312-314
5. Douglas NJ, Brash HM, Wraith PK, et al. Accuracy, sensitivity to carboxyhemoglobin, and speed of response of the Hewlett-Packard 47201 ear oximeter. Am Rev Respii Dis 1979;119:311-313
6. Yoshiya I, Shimada Y, Tanaka K. Spectrophotometric monitoring of arterial oxygen saturation in the fingertip. Med Biol Eng Comput 1980;18:27-32
7. Cecil WT, Petterson MT, Lamoonpun S, Rudolph CD. Clinical evaluation of the Biox IIA ear oximeter in the critical care environment. Respir Care 1985;30(3): 179-183

Monitoring Equipment: Wukitsch et ah Pulse Oximetry 301

8. Chapman KR, D'Urso B, Rebuck AS. The accuracy and response of a simplified ear oximeter. Chest 1983;83:860-864
9. Pologe J. Pulse oximetry: technical aspects. Int Anesth Clin 1987;25(3):142-153
10. Wukitsch MW. Pulse 0ximetry: historical review and Ohmeda functional analysis, tnt J Clin Monk Comput 1987;4:161-166
11. Gross J. Unprecedented rise in use of pulse oximetry reflects important advance in anesthesiology (interview). Anesthesiot News 1987;13(7):66,68-69
12. Southall DP, Bignalls S, Stebbens VA, et al. Pulse oximeter and transcutaneous arterial oxygen measurements in neonatal and paediatric intensive care. Arch Dis Child 1987;62:882-918
13. Taylor MB, Whitwam JG. The accuracy of pulse oximeters. Anaesthesia 1988;43:229-232
14. Scheller MS, Unger RJ. The influence of intravenously administered dyes on pulse oximetry readings. Anesthesiology 1986;65:$12
15. Sidi A, Paulus DA, Rush W, et al. Methylene blue and indocyanine green artifactually lower pulse oximetry readings of oxygen saturation. Studies in dogs. J Clin Monit 1987;3:249-256
16. Stewart RD. Carboxyhemoglobin levels in American blood donors. JAMA 1974;229:i187-1195
17. Barker SJ, Tremper KK, Hyatt J, Zaccari J. Effects of methemoglobinemia on pulse oximetry and mixed venous oximetry. Anesthesiology 1987;67:A171
18. Chaudhary BA, Burki NK. Ear oximetry in clinical practice. Am Rev Respir Dis 1978;117:173-175
19. AndersonJV. The accuracy of pulse oximetry in neonates: effects of fetal hemoglobin and bilirubin. J Perinatol 1987;7(4):323
20. Pologe JA, Raley DM. Effects of fetal hemoglobin on pulse oximetry. J PerinatoI t987;7(4):324-326
21. Yelderman M, New W, Jr. Evaluation of pulse oximetry. Anesthesiology 1983;50:349-352
22. Severinghaus JW, Naifeh KH. Accuracy of response of six pulse oximeters to profound hypoxia. Anesthesiology 1987;67:551-558
23. Payne JP, Severinghaus JW. Pulse oximetry. London: Springer-Verlag, t986:29-30
24. Kagle DM, Alexander CM, Berko RS, et al. Evaluation of the Ohmeda 3700 pulse oximeter: steady-state and transient response characteristics. Anesthesiology 1987; 66:375-380
25. Cecil WT, Morrison LS, Lamoonpun S. Clinical evaluation of the Ohmeda Biox III pulse oximeter: a comparison of finger and ear cuvettes. Respir Care 1985;30(10):840-850

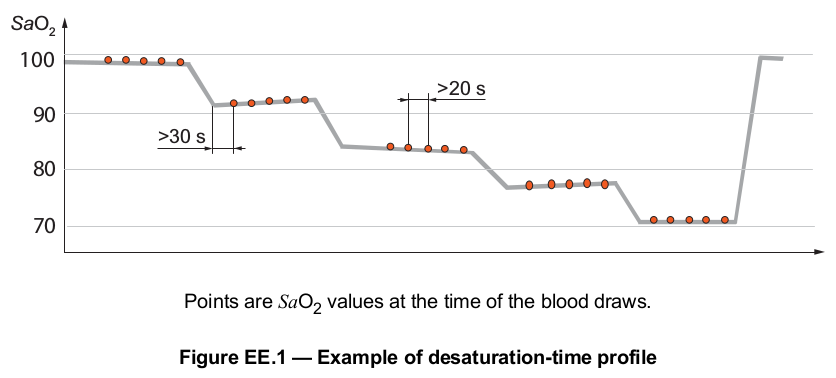
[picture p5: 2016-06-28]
ethics_application/Time-desaturation profile.png

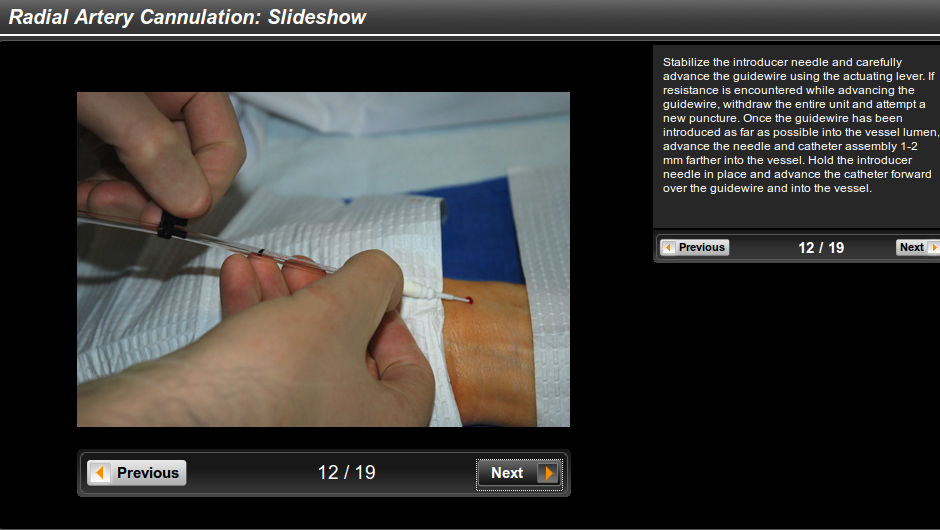
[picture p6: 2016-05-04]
ethics_application/radial_cannulation/radial_explainer_12.png

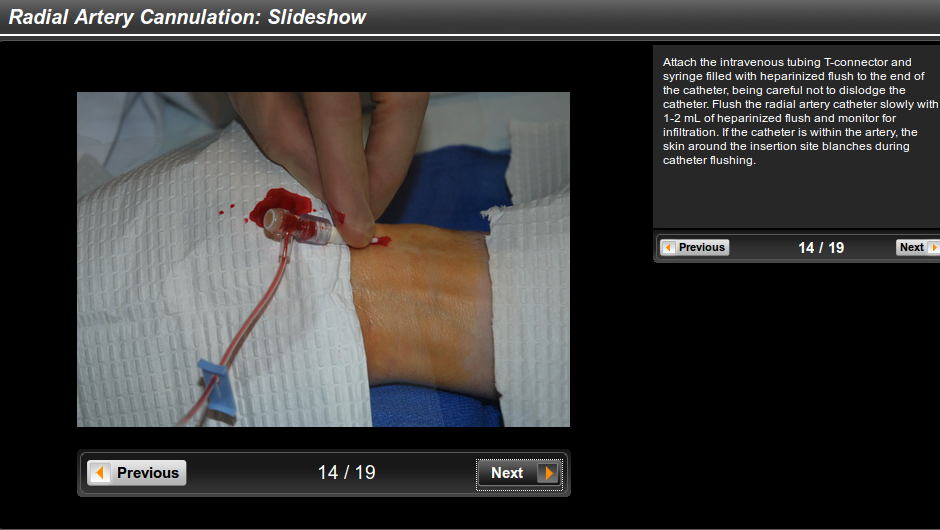
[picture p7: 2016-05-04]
ethics_application/radial_cannulation/radial_explainer_14.png

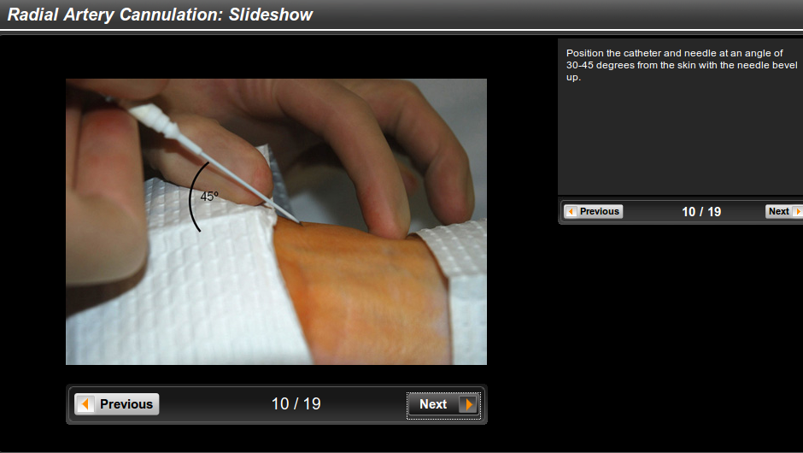
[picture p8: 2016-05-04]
ethics_application/radial_cannulation/radial_explainer_10.png

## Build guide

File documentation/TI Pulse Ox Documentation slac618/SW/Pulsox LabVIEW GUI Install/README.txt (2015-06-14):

All applicable SW can be downloaded via this URL- http://www.ti.com/lit/zip/slaa458

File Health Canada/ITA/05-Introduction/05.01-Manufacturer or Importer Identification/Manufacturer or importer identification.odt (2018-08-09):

Company Name | Glia Inc.
Street Address/P.O. Box: 54 Craig St. City: London Province/State: Ontario Postal/Zip Code: N6C 1E8 Country: Canada
Contact Name and Title: | Dr. Tarek Loubani, Primary investigator and Emergency Physician
Telephone No.: +1 519 488 6475 | | Fax No.: NA
E-Mail Address: | tarek@tarek.org

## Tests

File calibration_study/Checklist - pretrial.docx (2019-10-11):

Pretrial checklist

Welcome and go over consent

Ask to refrain from eating

Ask to use restroom prior to study

Ask about allergies and medical conditions

Go over exclusionary list in protocol

Be made aware of the max 2 attempts at ART line prior to exclusion.?? Must hold a hard line on this even if participant is resistant so being upfront about this is a must

Turn off alarms on monitors

Disable automatic blood pressure reading and make sure a timer is available/set for 5 minute intervals for manual BP

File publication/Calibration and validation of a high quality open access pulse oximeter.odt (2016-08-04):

Calibration and validation of a high-quality open access pulse oximeter

Alexander Pavlosky¹, Tarek Loubani1,2,3,4*

¹ Faculty of Medicine, University of Western Ontario, London, Ontario, Canada.

² Division of Emergency Medicine, Department of Medicine, University of Western Ontario, London, Ontario, Canada.

³ Division of Emergency Medicine, London Health Sciences Centre, London, Ontario, Canada

⁴ Division of Emergency Medicine, Al-Shifa Hospital, Gaza

* Corresponding author

E-mail: Tarek.Loubani@lhsc.on.ca

# Abstract

# Introduction

Pulse oximetry is an important tool used in high-income countries to assess a patient’s oxyhemoglobin saturation and is used diversely in medicine both in clinical and surgical settings. In the developed world, pulse oximetry has become the standard of care as it increases patient safety by alerting physicians to hypoxemia during anesthesia¹,², pneumonia³,⁴ and acute respiratory distress syndrome⁵. Currently, low and middle income countries are in need of an estimated one million pulse oximeters⁶, with only 41-70% of operating environments having access to a pulse oximeter in developing nations compared with 100% in developed nations⁷.To fill this need, previous groups have created lower cost pulse oximeters for use in low-income settings⁸⁻¹⁰.

In this article, we describe the design, calibration and validation of an open access pulse oximeter, known as the Glia pulse oximeter, at an estimated cost of under 25USD. The aim of the project is to provide free access to plans and software of the Glia pulse oximeter, allowing physicians around the world to build a Health Canada approved pulse oximeter that meets USA Food and Drug Administration (FDA) 501(k) certification for use in their clinic or operating room. To do so, the performance of the Glia pulse oximeter will be compared with arterial hemoglobin oxygen saturation (SaO2) as measured by blood gas analysis. In addition, performance testing comparing the calibrated Glia pulse oximeter to a standard Nellcor pulse oximeter will also be performed.

# Methods

Controlled Desaturation Study

The study was performed at Victoria Hospital, London Health Sciences Centre in London, Ontario. Before a desaturation procedure, volunteers were screened for exclusion criteria and informed written consent was obtained. FDA 501(k) protocols to test other pulse oximeter units was followed¹¹.

Volunteers were laid flat with one arm raised onto a table and a radial arterial catheter was inserted for SaO2 measurements. The Glia oximeter and CO-oximeter was applied to adjacent fingers on contralateral arm. A Respiract was used to measure background end-tidal PCO2 and PO2 and a desaturation sequence was modified for those values.

At the beginning of the experiment, control oximeter data and two blood samples were drawn while the volunteer was breathing medical air. The volunteer then breathed 100% O2 and a maximum SpO2 was obtained. A hypoxic gas mixture containing nitrogen, oxygen and carbon dioxide was used to serially desaturate the volunteer using the Respiract to an SpO2 of 96-92%, 91-87%, 86-82%, 81-77%, 76-72% and 71-67%. Each plateau was allowed to stabilize for 30 seconds and N oximeter readings and arterial samples were taken at each plateau 20 seconds apart.

1. Walker, I. & Wilson, I. Anaesthesia in developing countries - a risk for patients. Lancet 968–969 (2009).

2. Haynes, A., Weiser, T. & Berry, W. A surgical safety checklist to reduce morbidity and mortality in a global population. New Eng J Med 491–499 (2009).

3. Duke, T., Graham, S. & Cherian, M. Oxygen is an essential medicine: a call for international action. Int J Tuberc Lung Dis 1362–1368 (2010).

4. Ashraf, H., Jobayer, M. & Alam, N. Treatment of childhood pneumonia in developing countries.

5. Kwizera, A. & Dunser, M. A Global Perspective on Acute Respiratory Distress Syndrome and the Truth about Hypoxia in Resource-limited Settings. Am. J. Respir. Crit. Care Med. 5–7 (2016).

6. WHO. Global Pulse Oximetry Project. (2008).

7. Funk, L., Weiser, T. & Berry, W. Global operating theatre distribution and pulse oximetry supply: an estimation from reported data. Lancet 1055–1061 (2010).

8. Edwards, J. Taking the pulse of pulse oximetry in Africa. CMAJ 184, E244–E245 (2012).

9. G, D. et al. Accuracy of the Lifebox pulse oximeter during hypoxia in healthy volunteers. Anesthesia 68, 1220–1223 (2013).

10. L, F. et al. Evaluation of a large-scale donation of Lifebox pulse oximeters to non-physician anaesthetists in Uganda. Anaesthesia 69, 445–451 (2014).

11. U.S. Food and Drug Administration. 501(k) clearances. http://www.fda.gov/MedicalDevices/ProductsandMedicalProcedures/DeviceApprovalsandClearances/510kClearances/default.html. Accessed July 27,2016.

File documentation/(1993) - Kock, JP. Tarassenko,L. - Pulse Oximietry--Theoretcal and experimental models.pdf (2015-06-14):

### 1 Introduction

THE PULSE oximeter is a noninvasive optical instrument which measures arterial oxygen saturation (SaO2) in a pulsatile vascular bed such as the fingertip or earlobe. Sa02 is defined as:

C~ | x 100 per cent | (1) SaO 2 - Co q'- C r

where C o and C, are the concentrations of oxyhaemoglobin HbO2, and reduced haemoglobin (or deoxyhaemoglobin) Hb, in the blood sample. Pulse oximetry relies on the difference in absorption spectra between HbO 2 and Hb. Dual-wavelength measurements are usually made by placing a probe containing two light-emitting diodes (LEDs) whose spectral peaks are in the red and infra-red regions, and a photodiode on opposite sides of the vascular bed. The photodiode senses the light transmitted through the tissues, which comprises an alternating (AC) signal due to absorption by pulsatile arterial blood superimposed on a steady-state (DC) level arising from attenuation by venous blood, skin pigments and other nonpulsatile components. With most instruments, the DC level at each wavelength is used to normalise the corresponding AC signal amplitude. The ratio of these AC amplitudes at the two wavelengths has been shown to be a function of the arterial oxygen saturation, and this is the basis of the technique of pulse oximetry (WUKITSCH et al., 1988).
The first pulse oximeters were developed in Japan

First received 25th March and in final form 30th September 1991

### 9 IFMBE: 1993

Medical & Biological Engineering & Computing during the late 1970s. In this early work, whole blood was considered simply to be made up of Hb and HbO 2 solutions which obeyed the Beer-Lambert Law (YOSHIYA et al., 1980). This law describes the absorption of monochromatic light in the nonscattering solution:
I = I o 10 -`c~ | (2)
where I 0 and I are the incident and transmitted light intensities through a cuvette of depth D, containing a solution of concentration C and with an extinction coefficient e. Eqn. 2 may be rewritten in terms of optical density OD as:
OD=log(~)=~CD | (3)

Experience soon showed, however, that such a simple model gave a poor correlation between pulse oximeter readings and invasive measurements of arterial oxygen saturation (SHIMADA et al., 1984). For instance, at 80 per cent SaO 2 the pulse oximeter overestimated the saturation by approximately 5 per cent, an error which is clinically unacceptable.
As recognised by these early workers (SHIMADA et al., 1984), this discrepancy is due to light scattering phenomena. KRAMER et al. (1951), ANDERSON and SEKELJ (1967) and others had already conclusively shown that the Beer-Lambert law is not valid for whole blood, for which the optical density is nonlinear with respect to cuvette depth and haematocrit. In addition KRAMER et al. (1951) also reported that the optical density of whole blood is approximately 7-20 times greater than that of haemoglobin solutions. In whole blood, light scattering arises from the discontinuity in refractive index at the plasma/red blood
May 1993 | 291

cell interface, the wavelength of light in the red and infrared being of the same order of magnitude as the dimensions of a red blood cell. The high concentration of red blood cells in whole blood ensures that light scattered once is likely to be scattered again--hence the phenomenon of multiple scattering.
The complex optical properties of whole blood are such that, in practice, all commercial pulse oximeters are now empirically calibrated using procedures in which hypoxia is induced in normal subjects (SEvERINGHAUS and NAIFEH, 1987). As soon as steady-state hypoxia is reached, the values of the normalised red:infra-red ratio, and of SaO 2, as measured from an arterial blood sample, are recorded. If such data are collected from a large number of volunteers, over a range of oxygen saturations, an empirical calibration curve can be obtained. The majority of such tests are carried out when the SaO 2 is greater than 70 per cent, the lowest tolerable steady-state hypoxia. Below this saturation, the calibration curve is largely estimated by extrapolation.
In an attempt to develop a model relating SpO2* and dual-wavelength measurements on whole blood, we adopted a similar approach to that of STEINKE and SHEP-HERD (1986). To study the relative importance of scattering and absorption, they measured the optical density of whole blood as a function of haematocrit and also the optical density of haemolysed blood as a function of haemoglobin concentration. They then fitted a number of mathematical models for the optical properties of whole blood to their experimental data and found Twersky's multiple scattering theory (TW~RSKY, 1962; 1970a; b) to be the most appropriate. With the use of Twersky's theory they investigated the role of light scattering in whole blood oximetry and concluded that scattering effects did not affect the linearity of whole blood oximeters. Instead, scattering effects were said to increase the sensitivity of these oximeters by contributing linearly to the total optical density change that occurs with altered oxygenation (STEINKE and SHEPHERD, 1986).
To extend this approach to pulse oximetry, we measured the optical density of whole and also of haemolysed blood as a function of cuvette depth. We chose the latter variable rather than haematocrit in view of the fact that pulse oximeters rely on arterial volume pulsations which are essentially changes in optical pathlength. We fitted three different theoretical models of optical transmission in whole blood to our experimental data to determine which model might be the most applicable for the pulsatile case. The model which gave us the closest fit was then used to obtain a relationship between SaO 2 and our dual-wavelength measurements.

1.1 Optical theories of whole blood
Among the many theories proposed to study the optical properties of whole blood, three have found general acceptance: Zdrojkowsi and Pisharoty's approach based on photon diffusion theory, Twersky's analytical multiple scattering theory, and the Kubelka-Munk theory. All three approaches are now reviewed in the context of their applicability to pulse oximetry.

1.2 Photon diffusion theory
Photon diffusion theory, also known as radiative transfer theory, is based on observations of the transport char-
*Notation based on recommendation by PAYNE and SEVERINGHAUS (1986). Pulse oximeter readings are denoted by SpO 2 and direct in vitro measurements from arterial blood samples are denoted by 5"aO 2 .
292

acteristics of wave intensities. It relies on a differential equation called the equation of transfer which is equivalent to the Boltzmann equation used in the kinetic theory of gases (ISHIMARU, 1978; JOHNSON, 1970). ZDROJKOWSK! and PISHAROTY (1970) solved the diffusion equation for a collimated light beam incident on a slab of blood incorporating the concept of mean optical pathlength of photons in dense scattering media previously derived by SHOCKLEu (1962). Zdrojkowski and Pisharoty derived the following optical density equation of whole blood:

OD = --log e -~e + S(B2 _ Q2) sinh (Qd)

x{1-e-~d(cosh(Qd)+~sinh B | (Qd))} 1 | (4)

where
1 1
8 | = - | + - | (5)
| L | S
Q = ~ | (6)
So(;j S = | (7)
H(H - | - | 1)
log (e)
L--- | • 1-64 | (8)
~Cub
and L is the mean optical path travelled by a photon before absorption, S is the mean optical path before scattering, e is the extinction coefficient in litre mmol-1 cm 1, Cub is the concentration of haemoglobin in the whole blood sample in g dl- ~, H the fractional haematocrit and d the cuvette depth.

1.3 Twersky's analytical multiple scatterin9 theory Twersky's analytical multiple scattering theory of light by large low-refracting and absorbing particles is based on electromagnetic wave theory (TWERSKY, 1962; 1970a; b). Twersky started by first considering the scattering and absorption effects of a single particle, and then introduced the interaction of many particles and statistical averages to finally arrive at an analytical solution to the multiple scattering problem. ANDERSON and SEKELJ (1967), LIPOWSKY et al. (1980) and STEINKE and SHEPHERD (1986) have shown this theory to be applicable to whole blood. Twersky's equation for the variation of optical density is as follows:

-- loglo [(1 -- q)10 -p + ql0 -~] | (9)
where
fl = aOH(1 -- H) | (10)
2q'maDH(1 -- H)
6 = | (11)
2m + aD(1 -- H)
eCD
m = | (12)
H
and
a = constant depending on particle size, wavelength, photodiode aperture and refractive indices of plasma and red blood cells
Medical & Biological Engineering & Computing May 1993 q = constant depending on particle size, wavelength and refractive indices
q' = constant depending on the optical arrangement.
The above equation may be interpreted as follows: the eCD term is that given by the Beer-Lambert Law; it represents absorption OD,bs and is linear with respect to haematocrit. The second term is a measure of the coherent and incoherent scattering OD~cat. It is a parabolic function of H and is symmetric about H = 0.5. One of the most interesting features of this model is that the total optical density ODto t can be resolved into two distinct and independent parts; thus ODto t = ODsc.t + ODab s (STEINKE and SHEPHERD, 1986).

haemolysed blood requires two separate systems: an extracorporeal blood circuit and a standard spectrophotometric arrangement.

2.1 In vitro blood circuit
A closed-loop extracorporeal blood circuit is used to simulate gas exchange at the lungs, pulsatile blood flow and a vascular bed. The blood circuit is shown in Fig. 1. It comprises a reservoir, peristaltic pump, seven cuvettes and an extracorporeal membrane oxygenator. Such a system allows the oxygen saturation, pH and flow rate of the blood to be varied in a controlled manner.

1.4 Two-flux Kubelka-Munk theory
The Kubelka-Munk theory is a phenomenological approach based on two light fluxes travelling in opposite directions in a homogeneous slab of material which exhibits scattering and absorption effects (KuBELKA and MUNK, 1931; JANSSEN, 1972; ISHIMARU, 1978). This theory assumes diffuse monochromatic illumination of the sample, random distribution of particles whose size is small compared with the sample thickness, negligible specular reflection, and finally isotropic scattering in the medium. These assumptions allow two coupled differential equations to be derived. The solution leads to the following results:
(1 - | O)e -~a
OD - 1-- Oe 2,d | (13)

where
~z = x/K z + 2KS | (14)

S+K --~
0 - | (15)
S+K+o~
and S and K are the scattering and absorption coefficients, respectively.
The major advantage of this approach is that a simple closed form solution is obtained with only two constants: S and K. Unfortunately, the range of its validity and its theoretical basis are not well established and the two coefficients must be determined experimentally.

### 2 Materials and methods

The experimental determination of the relationship between optical density and cuvette depth for whole and

### capnograph l

T

/[~ | | reservoir
J | J extracorporeal J | [ membrane
~T | j oxygenator peristaltic p~.~
m, er I | I | ,k | /
t t t ' ~seven | cuvettesinseries~ ~'-~"
N' 2 C~ 2 C02 | sapPrl;ng | rP hOtOdiOde
photodiode | voltmeter
| amplifier

### Fig. 1 Blood circuit used in the in vitro experiments

2.2 The cuvette
The cuvettes are used to simulate blood flow through a vascular bed such as the fingertip or earlobe. The cuvettes essentially consist of a blood compartment sandwiched between two diffusers and thick layers of clear Perspex as shown in Fig. 2. Of course, this is a simplified model as no attempt is made to reproduce the anatomical network of capillaries, arterioles and venules.

### movable LED holder clear Perspex black Perspex

diffu

photodiode holder J, | ,J | blood film
12mm
22 mm
Fig. 2 Cross-section of the cuvette and LED/photodiode arrangement used for optical density measurements
To measure the optical density as a function of cuvette depth seven cuvettes were constructed with blood compartment depths of 0.20, 0'50, 0'75, 0.92, 1.15, 1.39 and 1.57 mm. The accurate measurement of cuvette depth was critical and hence the gaps, or depths, were measured after construction with feeler gauges. The relatively thick layers of Perspex around the blood film ensured that the depth of the blood film remained constant despite the pressure variations caused by the peristaltic pump. The blood inlets and outlets of the cuvettes were tapered to prevent flow separation.
The central 'window' of 12mm diameter was made of clear Perspex and contained two diffusers made from translucent paper which had a very flat absorption spectrum in the wavelength range of interest. These diffusers were essential to simulate the optical properties of skin and other tissues. The penetration depth t in human tissue in the red to near-infra-red part of the spectrum has been found to be in the order of a few millimetres (WILSON and ADAM, 1983; ANDERSON and PARRISH, 1981). Hence, for a finger or earlobe of thickness 5-15ram, the incident light gradually becomes diffuse as it penetrates the tissue and blood within it.

t The depth at which collimated light becomes perfectly diffuse and is attenuated by 63 per cent according to photon diffusion theory.
Medical & Biological Engineering & Computing | May 1993 | 293

To investigate the effectiveness of the diffusers in our cuvettes, the intensity profile and angular distribution of the light incident on the blood film itself were measured (DE KOCK, 1991). The half-power diameters of the circular intensity profiles were found to be 2.5 and 4.5mm for the red and infra-red LEDs, respectively. The half-power angles were found to be 29 ~ and 38 ~ for the red and infrared LEDs, respectively. These figures showed that the diffusers were not ideal but they did provide spatial and angular averaging of the incident light which resulted in smoothing out of the variations in optical pathlengths in the blood film. However, the blood film itself is highly scattered at the haematocrits used, and the penetration depth of light in whole blood at the wavelengths employed in pulse oximetry is no more than 0.3-0.5mm (TAKATANI et al., 1980). Thus the combination of diffuser and blood film ensured that it was diffuse light which interacted with the bulk of the blood as in vivo. A diffuser was also located in front of the photodiode and thus increased its acceptance angle; hence the detected transmitted light would originate from a larger and more spatially averaged area. The remainder of the cuvette was made of black Perspex to prevent stray light from interfering, and to eliminate light absorption by blood at the cuvette walls, where the blood flow may have been affected by boundary conditions.

inlets and outlets. The same gas as used by the membrane lung was also allowed to flow through the dead space above the blood in the reservoir. All the components of the blood circuit were connected together by PVC tubing (Portex, 4 mm inner diameter and 6 mm outer diameter).

2.5 Optical system
The optical density was measured using LEDs as light sources and a p-i-n photodiode as detector. The centre wavelengths of the LEDs were 660nm (red, TLMP7005, Three-Five Systems Inc.) and 950nm (infra-red, CQW13, TFK Inc.) and were typical of those used in pulse oximetry. A simple feedback circuit was used to provide a constant, but controllable, current to each LED. Once an LED had reached its operating temperature, the arrangement gave a light output which was very nearly constant. The LEDs were mounted in a separate holder which clamped onto the detector bracket at a predetermined position. In addition, each cuvette had location guides which allowed the LED/photodiode arrangement to be moved from cuvette to cuvette to allow for readings at the two wavelengths and for different depths on the same blood sample. The transmitted light intensity was detected by a p-i-n photodiode (Stanley PP210), and converted to a voltage using a standard transimpedance amplifier circuit.

2.3 Pump
The peristaltic pump (Marlow-Watson type MHRE881) produced a pulsatile blood flow to simulate cardiac output through the cuvette, membrane lung, and up to the reservoir. The pump generated sinusoidal output, at 70 cycles min-1, to produce a mean flow rate of approximately 20mlmin 1. A pump, rather than an elevated reservoir, was used because it was a better approximation to physiological conditions. Even with rigid cuvettes under these conditions, the transmitted light signal had a small pulsatile component (due to the changing orientations of the red blood cells). As we were interested in changes in light transmission due to volume changes (simulated here by cuvettes of different depths), the pulsatile component was filtered out.

2.4 Extracorporeal membrane oxygenator
An extracorporeal membrane oxygenator was used to control the oxygen saturation and pH of the blood. The membrane lung was composed of a single flat blood channel of 0-5mm depth, sandwiched between two flat microporous isotactic polypropylene membranes (Celgard 2402) which were mounted against rigid support ribs on the gas side (DORRINGTON et al., 1985). The device had an active area of 64 x 160mm 2 but a very small prime volume of only 5.1 ml.
A gas mixer was used to adjust the composition of the gas entering the membrane oxygenator by controlling the partial pressures of 02, N2 and CO2 in the blood, the relative partial pressures of N 2 and O2 determining the oxygen saturation. The partial pressure of CO2 needed to be kept at approximately 5 kPa to maintain the blood pH at the right level. A capnograph (Gould Godhart Mark III) monitored the CO 2 content of the gas at the output of the membrane lung. The flow rate of CO2 was adjusted to give a 5 per cent (+0.5 per cent) CO2 content at all times. The gas was finally vented to the atmosphere.
The reservoir had a volume of 60 ml, with blood inlet at the top and outlet at the bottom. There were also gas

2.6 Experimental procedure
Outdated whole human blood was obtained from the local Blood Transfusion Service. The blood was thoroughly mixed and filtered through a fine fabric mesh to remove aggregates and then centrifuged at 3000 rev min-1 for 20min, to separate the red blood cells (RBCs) and plasma. The packed RBCs were resuspended in isotonic phosphate buffered saline (PBS) and recentrifuged. This washing procedure was repeated three times. After the final centrifugation, a 100ml blood sample of 15.8 gd1-1 haemoglobin concentration (as measured by a Radiometer OSM-3 Hemoximeter) was made up by mixing appropriate amounts of packed red blood cells and PBS. The haematocrit level of the blood sample was found to be 50 _+ 2 per cent as measured by the microcapillary method. The concentrations of carboxyhaemoglobin and methaemoglobin were always found to be less than 1 per cent as measured by the Hemoximeter, and hence would not have caused any significant error.
The following experiment was performed to measure the relationship between optical density and cuvette depth for whole blood over a wide range of oxygen saturations. The blood sample was introduced into the blood circuit, and a mixture of 95 per cent oxygen and 5 per cent CO z was allowed to flow through the membrane lung and reservoir. The system was then given time to saturate fully and equilibrate to room temperature. The oxygen saturation SaO 2 was verified to be 98-100 per cent by the Hemoximeter. At this point, the transmitted light intensity I for each of the seven cuvettes was recorded at both wavelengths. To desaturate the blood, the oxygen passing through the membrane lung was replaced by a mixture of 95 per cent N 2 and 5 per cent CO2.
As the saturation slowly reduced over a period of 3 h, the light intensity readings, as described above, were taken at intervals corresponding to changes in SaO z of approximately 10 per cent. The saturation levels were measured just before and just after the light intensity readings using the Hemoximeter, and remained constant to within 3 per cent of the initial measurement (this variation being caused by having to take measurements on seven cuvettes in turn).
294 | Medical & Biological Engineering & Computing | May 1993

With the use of an N 2 and CO2 gas mixture, it was very difficult to desaturate the blood fully; to obtain readings at 0 per cent saturation, a small quantity of a chemical reduction agent, sodium hydrosulphite (Na2S204) , was added until the oxygen saturation dropped to less than 0.5 per cent SaO 2 (as measured by the Hemoximeter). Finally, the blood was removed from the system by flushing and rinsing with water. After replacing the water with PBS, the value of Io was recorded for each cuvette at both wavelengths.
The above experiment was also repeated with haemoglobin solutions. The latter were prepared by washing whole blood samples in PBS as described previously and then haemolysing them by ultrasound disruption. The red blood cell ghosts were precipitated by ultracentrifugation for 30 min at 32 000 rev min-1. Haemolysis was verified by microscopic examination. Readings were only taken for fully oxygenated and fully deoxygenated haemoglobin solutions at the concentration of 15.8gd1-1, as only the Hb and HbO 2 extinction coefficients were required for the theoretical model based on the Beer-Lambert law relating Sa02 and the R:IR ratio.
From the data gathered with this set of experiments, it was possible to obtain plots of optical density against cuvette depth for whole blood over the entire saturation range at approximately 10 per cent SaO 2 intervals and for Hb and HbO 2 solutions at wavelengths of 660 and 950 nm.
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

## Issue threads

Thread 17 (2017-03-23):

### ISSUE TITLE
Question: Instructions?

### ISSUE THREAD

**Issue by ckrozean** [GliaX/pulseox#17]
Are there step-by-step instruction? I purchased parts from the bill of materials with the hope of assembling one of these devices. However, I can't seem to find instructions on how to start.

**Comment by tareko** [comment]
No instructions exist yet. In essence, assemble all parts to their
locations on the board.

Do you have a copy of the PCB made? Perhaps we can work together to make
instructions for others.

tarek : )

**Comment by ckrozean** [comment]
Not at this time. I'm very much new to this. Where can I get a pcb made? 
I would be willing to collaborate on instructions!
Thanks!
Colby Rozean
Texas Tech University – Mechanical Engineering
(806)-831-9391
ckrozean@gmail.com




On Fri, Sep 25, 2015 at 1:22 AM -0700, "Tarek Loubani" <notifications@github.com> wrote:










No instructions exist yet. In essence, assemble all parts to their

locations on the board.



Do you have a copy of the PCB made? Perhaps we can work together to make

instructions for others.



tarek : )

**Comment by tareko** [comment]
Hi Colby,

I'm going to close this for now. If you're still interested, it looks like we're going to have some substantial forward momentum in the next few months, so keep an eye out on the project!

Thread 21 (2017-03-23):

### ISSUE TITLE
Code example of max30100

### ISSUE THREAD

**Issue by SloMusti** [GliaX/pulseox#21]
An example of code for processing measurement values: https://morf.lv/implementing-pulse-oximeter-using-max30100

**Comment by tareko** [comment]
Excellent. out of curiosity, did you find that on hackaday or somewhere else? I have looked at this chip, and it features in an alternative design by @cfalc. However, it uses reflective rather than transmission pulse oximetry, and also doesn't seem able to add more LEDs. The explanation of how, though, is definitely applicable..

tarek : )

**Comment by SloMusti** [comment]
Yes, have seen it on Hackaday. This is mainly useful to get more ideas about data processing required.

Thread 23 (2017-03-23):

### ISSUE TITLE
LED circuit

### ISSUE THREAD

**Issue by VojislavM** [GliaX/pulseox#23]
IR LEDs are driven by MCU, which is not a good idea, maybe it is beater to drive them with small H bridge. For example, the diode from BOM is needs 20 mA of forward current, and the STM MCU is able to provide ~20 mA output current source by any I/O and control pin. Is to close, and it may burn the IO Pin of the MCU.

**Comment by kliment** [comment]
The emitters are on for very short pulses, tens of microseconds, so the current limiting is done by PWM. At a supply voltage of 3V the emitters don't reach their rated current even when continuously on, so in practice the current is below even the continuous rated current. We had series limiting resistors on the emitter lines but after measuring the effective current we removed them as they were not necessary. I'd prefer to avoid the extra complexity of an h-bridge, both for BOM cost reasons and to keep the layout single-sided.

**Comment by VojislavM** [comment]
Great, I am glad to hear that you already tested this. I did not know for how long are the LEDs on.

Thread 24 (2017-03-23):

### ISSUE TITLE
pulse oximeter circuit

### ISSUE THREAD

**Issue by VojislavM** [GliaX/pulseox#24]
why not use integrated pulse oximeter instade of IR LEDs and receiver?

**Comment by tareko** [comment]
Such as the MAX30100? @CFalc is working on [a model that uses an integrated chip](https://github.com/CFalc/Make-your-own-Pulse-Oximeter) which we'll also probably test. It's arduino-based and failed with LED / receiver combo in [its original iteration](https://github.com/GliaX/oximeter).

In response to the question of why *this* model doesn't use it, the main reason is that we want to add several more LEDs in the future to cover carboxyhemoglobin and methemoglobin. The current market offering [uses 8 LEDs to accomplish this](http://www.masimo.com/home/rainbow-pulse-co-oximetry/technology-overview/), but it can probably be done with 4 or so, which is why this model has several open spots for more LEDs.

**Comment by VojislavM** [comment]
Thank you for the explanation.

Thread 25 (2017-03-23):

### ISSUE TITLE
Piezo speaker circuit

### ISSUE THREAD

**Issue by VojislavM** [GliaX/pulseox#25]
Piezo speaker is driven by the MCU pin, which is not a good idea, maybe it is better to drive it with small MOSFET. This is not so problematic because Piezo uses only 1 mA, but it is good practice to use MOSFET.

**Comment by kliment** [comment]
The piezo cannot be driven through a single high or low side FET because it must be both actively charged and actively discharged, so a push-pull configuration is necessary. The currents are very low, the system works well, and the MCU is quite resilient, so I see no reason to add complexity here.

**Comment by VojislavM** [comment]
Ok, I agree.

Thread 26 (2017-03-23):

### ISSUE TITLE
Power supply circuit

### ISSUE THREAD

**Issue by VojislavM** [GliaX/pulseox#26]
Why are there two power regulators?

**Comment by kliment** [comment]
It's a boost regulator with passthrough to allow operating from a single battery, down to 0.7V, followed by an LDO to allow a 3.3V or 5V supply to be used as well. The operating voltage of the device is 3V.

**Comment by VojislavM** [comment]
I did not know what was the input, but I assumed it was something like that. Thanks for the explanation.

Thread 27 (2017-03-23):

### ISSUE TITLE
Power connector PCB

### ISSUE THREAD

**Issue by VojislavM** [GliaX/pulseox#27]
Two pin jumper is not the best solution for connecting power to the device. What is the power source for this device and how is it connected?

**Comment by kliment** [comment]
The idea was to solder battery holder wires directly to the pads, rather than use a jumper. The jumper however was very convenient for testing and also has a footprint that is easy to solder wires to.

**Comment by VojislavM** [comment]
That is ok for testing.

**Comment by tareko** [comment]
The end goal here is to allow the device to be connected either via battery or another external supply as able (e.g., wall, other device, etc.)

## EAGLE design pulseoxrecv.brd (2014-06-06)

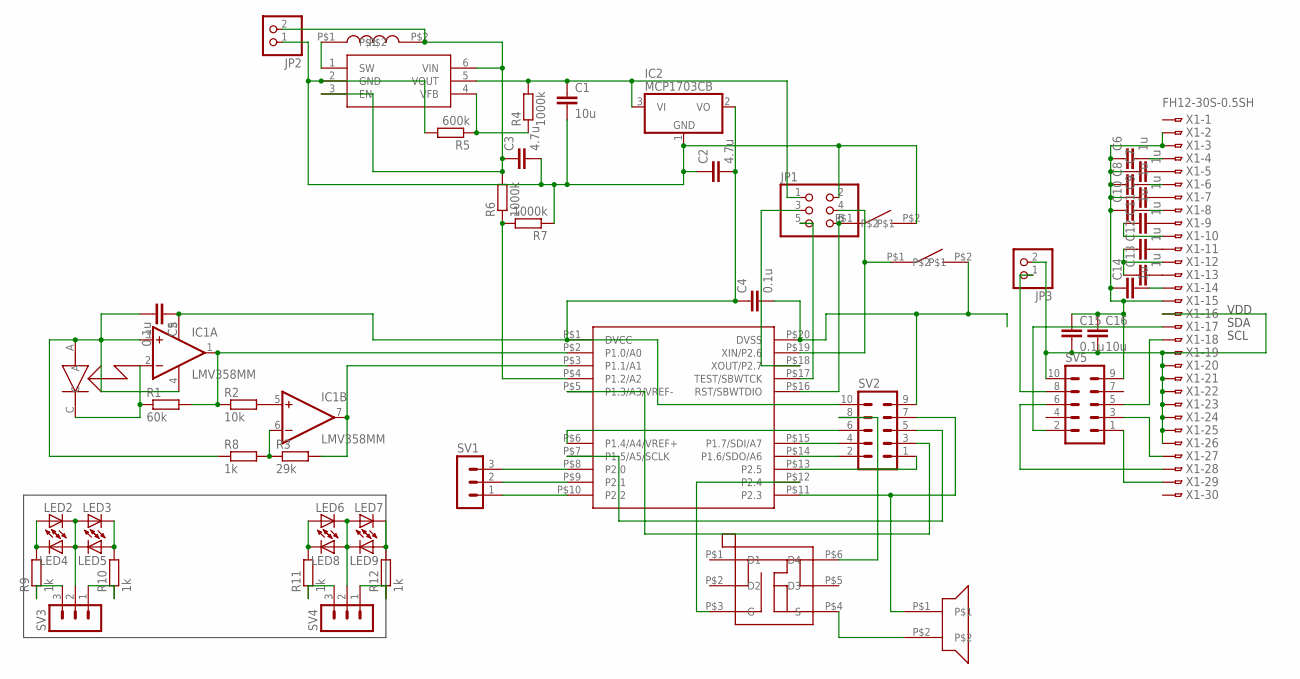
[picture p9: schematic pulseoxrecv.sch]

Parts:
C1, C16: 10u; C0603K
C2, C3: 4.7u; C0603K
C4, C5, C15: 0.1u; C0603K
C6, C7, C8, C9, C10, C11, C12, C13, C14: 1u; C0603K
IC1: LMV358MM; MSOP08
IC2: MCP1703CB; SOT23
JP1: PINHD-2X3; 2X03
JP2, JP3: PINHD-1X2; 1X02
LED1: QSB34ZR; R-PLCC2
LED2, LED3, LED4, LED5, LED6, LED7, LED8, LED9: LEDCHIP-LED0603; CHIP-LED0603
R1: 60k; R0603
R2: 10k; R0603
R3: 29k; R0603
R4, R6, R7: 1000k; R0603
R5: 600k; R0603
R8, R9, R10, R11, R12: 1k; R0603
SV1, SV3, SV4: MA03-1
SV2, SV5: MA05-2
U$1: MSP430G2452IPW20; TSSOP-20
U$2: MCP1640SOT23-6; SOT23-6L
U$3: WE-TPC
U$4: BSD816SN; SOT363
U$5, U$6: FSMSM
U$7: AT-2440-TWT-R
X1: FH12-30S-0.5SH

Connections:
3V: C2.2, C4.1, C5.1, IC1.8 (V+), IC2.2 (VO), SV2.10, U$1.P$1 (DVCC)
GND: C1.2, C2.1, C3.2, C4.2, C5.2, IC1.3 (+IN), IC1.4 (V-), IC2.1 (GND), JP1.2, JP2.1, LED1.A, R5.2, R7.1, R8.1, SV2.9, U$1.P$20 (DVSS), U$2.2 (GND), U$4.P$4 (S), U$5.P$2, U$6.P$2, U$7.P$2
unnamed: IC1.2 (-IN), LED1.C, R1.1
unnamed: SV2.4, U$1.P$15 (P1.7/SDI/A7)
unnamed: IC1.1 (OUT), R1.2, R2.1, U$1.P$2 (P1.0/A0)
unnamed: IC1.5 (+IN), R2.2
unnamed: IC1.6 (-IN), R3.1, R8.2
unnamed: IC1.7 (OUT), R3.2, U$1.P$3 (P1.1/A1)
unnamed: SV2.2, U$1.P$14 (P1.6/SDO/A6)
unnamed: C1.1, IC2.3 (VI), JP1.1, R4.2, U$2.5 (VOUT)
unnamed: U$2.1 (SW), U$3.P$1
unnamed: R4.1, R5.1, U$2.4 (VFB)
unnamed: C3.1, JP2.2, R6.2, U$2.3 (EN), U$2.6 (VIN), U$3.P$2
unnamed: SV1.1, U$1.P$10 (P2.2)
unnamed: SV1.2, U$1.P$9 (P2.1)
unnamed: SV1.3, U$1.P$8 (P2.0)
unnamed: R6.1, R7.2, U$1.P$4 (P1.2/A2)
unnamed: SV2.1, U$1.P$13 (P2.5)
unnamed: U$1.P$12 (P2.4), U$4.P$3 (G)
unnamed: SV2.7, U$1.P$11 (P2.3), U$7.P$1
unnamed: SV2.3, U$1.P$5 (P1.3/A3/VREF-)
unnamed: SV2.6, U$1.P$6 (P1.4/A4/VREF+)
unnamed: SV2.5, U$1.P$7 (P1.5/A5/SCLK)
unnamed: SV2.8, U$4.P$6 (D4)
unnamed: LED2.C, LED3.A, LED4.A, LED5.C, SV3.2
unnamed: LED2.A, LED4.C, R9.2
unnamed: LED3.C, LED5.A, R10.2
unnamed: R9.1, SV3.3
unnamed: R10.1, SV3.1
unnamed: LED6.C, LED7.A, LED8.A, LED9.C, SV4.2
unnamed: LED7.C, LED9.A, R12.2
unnamed: LED6.A, LED8.C, R11.2
unnamed: JP1.4, U$1.P$19 (XIN/P2.6), U$6.P$1
unnamed: R11.1, SV4.3
unnamed: R12.1, SV4.1
unnamed: JP1.3, U$1.P$18 (XOUT/P2.7)
unnamed: JP1.5, U$1.P$17 (TEST/SBWTCK)
unnamed: JP1.6, U$1.P$16 (RST/SBWTDIO), U$5.P$1
unnamed: SV5.5, X1.18
unnamed: C7.2, X1.5
unnamed: C9.2, X1.7
unnamed: C6.2, X1.4
unnamed: C8.2, X1.6
unnamed: C10.2, X1.8
unnamed: C6.1, C7.1, C8.1, C9.1, C10.1, C14.1, C15.1, C16.1, SV5.9, X1.2, X1.3, X1.15
unnamed: C11.2, X1.9
unnamed: C11.1, X1.10
unnamed: C12.2, X1.11
unnamed: C13.2, X1.13
unnamed: C12.1, C13.1, X1.12
unnamed: C14.2, X1.14
unnamed: C15.2, C16.2, JP3.2, SV5.10, X1.16, X1.19, X1.20, X1.21, X1.22, X1.23, X1.24, X1.25, X1.26
unnamed: SV5.2, X1.17
unnamed: SV5.1, X1.29
unnamed: SV5.6, X1.28
unnamed: SV5.3, X1.27
unnamed: JP3.1, SV5.8

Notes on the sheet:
SDA
SCL
VDD

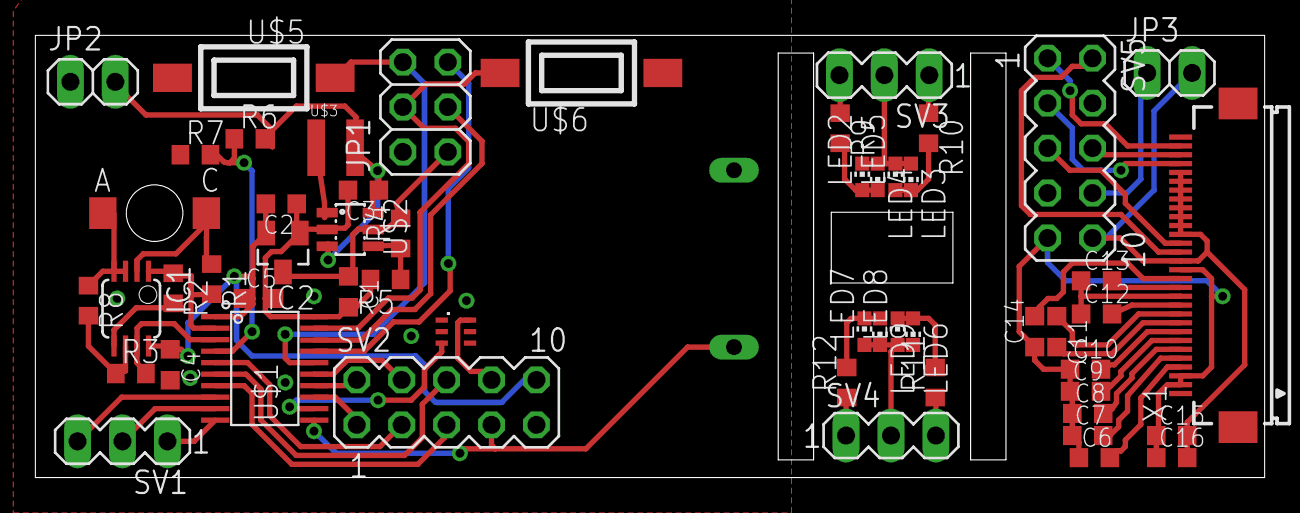
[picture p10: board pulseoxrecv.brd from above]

Board: 2 copper layers, 69.5 x 25.0 mm, 55 parts (0 on the bottom side), 57 nets.

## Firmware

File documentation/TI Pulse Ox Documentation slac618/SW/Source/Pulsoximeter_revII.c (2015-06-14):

/* --COPYRIGHT--,BSD
 * Copyright (c) 2012, Texas Instruments Incorporated
 * All rights reserved.
 *
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
 * *  Redistributions of source code must retain the above copyright
 *    notice, this list of conditions and the following disclaimer.
 *
 * *  Redistributions in binary form must reproduce the above copyright
 *    notice, this list of conditions and the following disclaimer in the
 *    documentation and/or other materials provided with the distribution.
 *
 * *  Neither the name of Texas Instruments Incorporated nor the names of
 *    its contributors may be used to endorse or promote products derived
 *    from this software without specific prior written permission.
 *
 * THIS SOFTWARE IS PROVIDED BY THE COPYRIGHT HOLDERS AND CONTRIBUTORS "AS IS"
 * AND ANY EXPRESS OR IMPLIED WARRANTIES, INCLUDING, BUT NOT LIMITED TO,
 * THE IMPLIED WARRANTIES OF MERCHANTABILITY AND FITNESS FOR A PARTICULAR
 * PURPOSE ARE DISCLAIMED. IN NO EVENT SHALL THE COPYRIGHT OWNER OR
 * CONTRIBUTORS BE LIABLE FOR ANY DIRECT, INDIRECT, INCIDENTAL, SPECIAL,
 * EXEMPLARY, OR CONSEQUENTIAL DAMAGES (INCLUDING, BUT NOT LIMITED TO,
 * PROCUREMENT OF SUBSTITUTE GOODS OR SERVICES; LOSS OF USE, DATA, OR PROFITS;
 * OR BUSINESS INTERRUPTION) HOWEVER CAUSED AND ON ANY THEORY OF LIABILITY,
 * WHETHER IN CONTRACT, STRICT LIABILITY, OR TORT (INCLUDING NEGLIGENCE OR
 * OTHERWISE) ARISING IN ANY WAY OUT OF THE USE OF THIS SOFTWARE,
 * EVEN IF ADVISED OF THE POSSIBILITY OF SUCH DAMAGE.
 * --/COPYRIGHT--*/
//*****************************************************************************
//    MSP430FG437 based pulse oximeter demonstration - Version II
//    V. Chan and S. Underwood
//    May 2005
//    Modified by Bhargavi Nisarga
//    April 2008
//*****************************************************************************
#include  <msp430xG43x.h>
#include "stdint.h"
#include "intrinsics.h"
#include "math.h"

// LCD Segment Configuration
#define seg_a       0x01
#define seg_b       0x02
#define seg_c       0x04
#define seg_d       0x08
#define seg_e       0x40
#define seg_f       0x10
#define seg_g       0x20
#define seg_h       0x80

#define NUM_0   (seg_a | seg_b | seg_c | seg_d | seg_e | seg_f)
#define NUM_1   (seg_b | seg_c)
#define NUM_2   (seg_a | seg_b | seg_d | seg_e | seg_g)
#define NUM_3   (seg_a | seg_b | seg_c | seg_d | seg_g)
#define NUM_4   (seg_b | seg_c | seg_f | seg_g)
#define NUM_5   (seg_a | seg_c | seg_d | seg_f | seg_g)
#define NUM_6   (seg_a | seg_c | seg_d | seg_e | seg_f | seg_g)
#define NUM_7   (seg_a | seg_b | seg_c)
#define NUM_8   (seg_a | seg_b | seg_c | seg_d | seg_e | seg_f | seg_g)
#define NUM_9   (seg_a | seg_b | seg_c | seg_d | seg_f | seg_g)
#define NUM_A   (seg_a | seg_b | seg_c | seg_e | seg_f | seg_g)
#define NUM_B   (seg_c | seg_d | seg_e | seg_f | seg_g)
#define NUM_C   (seg_a | seg_d | seg_e | seg_f)
#define NUM_D   (seg_b | seg_c | seg_d | seg_e | seg_g)
#define NUM_E   (seg_a | seg_d | seg_e | seg_f | seg_g)
#define NUM_F   (seg_a | seg_e | seg_f | seg_g)

const unsigned char hex_table[] =
{
    NUM_0,NUM_1,NUM_2,NUM_3,NUM_4,NUM_5,NUM_6,NUM_7,
    NUM_8,NUM_9,NUM_A,NUM_B,NUM_C,NUM_D,NUM_E,NUM_F
};

int32_t mul16(register int16_t x, register int16_t y);
                                           
//FIR filter coefficient for removing 50/60Hz and 100/120Hz from the signals
#if 0 
static const int16_t coeffs[9] =
{
    5225,
    5175,
    7255,
    9453,
    11595,
    13507,
    15016,
    15983,
    16315
};
#else
static const int16_t coeffs[12] =
{
    688,
    1283,
    2316,
    3709,
    5439,
    7431,
    9561,
    11666,
    13563,
    15074,
    16047,
    16384
};
#endif

// SaO2 Look-up Table
const unsigned int Lookup [43] = {100,100,100,100,99,99,99,99,99,99,98,98,98,98,
                                  98,97,97,97,97,97,97,96,96,96,96,96,96,95,95,
                                  95,95,95,95,94,94,94,94,94,93,93,93,93,93};
//
//  #define FIRST_STAGE_TARGET_HIGH         3900
//  #define FIRST_STAGE_TARGET_LOW          3600
//  #define FIRST_STAGE_TARGET_HIGH_FINE    4096
//  #define FIRST_STAGE_TARGET_LOW_FINE     3500

// LED Target Range 
#define FIRST_STAGE_TARGET_HIGH         3500
#define FIRST_STAGE_TARGET_LOW          3000
#define FIRST_STAGE_TARGET_HIGH_FINE    4096
#define FIRST_STAGE_TARGET_LOW_FINE     2700
#define FIRST_STAGE_STEP                5
#define FIRST_STAGE_FINE_STEP           1

// UART Transmission Structure Definition
enum scope_type_e
{
    SCOPE_TYPE_OFF = 0,
    SCOPE_TYPE_HEART_SIGNALS,
    SCOPE_TYPE_RAW_SIGNALS,
    SCOPE_TYPE_LED_DRIVE,
};
int scope_type = SCOPE_TYPE_HEART_SIGNALS;
//int scope_type = SCOPE_TYPE_RAW_SIGNALS;

int ir_dc_offset = 2000;
int vs_dc_offset = 2000;
int ir_LED_level;
int vs_LED_level;
int ir_sample;
int vs_sample;
char is_IR; 
int ir_heart_signal;
int vs_heart_signal;
int ir_heart_ac_signal;
int vs_heart_ac_signal;
unsigned int rms_ir_heart_ac_signal;
unsigned int rms_vs_heart_ac_signal;
int32_t ir_2nd_dc_register = 0;
int32_t vs_2nd_dc_register = 0;
unsigned long log_sq_ir_heart_ac_signal;
unsigned long log_sq_vs_heart_ac_signal;
unsigned long sq_ir_heart_ac_signal;
unsigned long sq_vs_heart_ac_signal;
unsigned int pos_edge = 0;
unsigned int edge_debounce;
unsigned int heart_beat_counter;
unsigned int log_heart_signal_sample_counter;
unsigned int heart_signal_sample_counter;

volatile unsigned int j;

/* The results */
unsigned int heart_rate;
unsigned int heart_rate_LSB = 0;
unsigned int SaO2, Ratio;
unsigned int SaO2_LSB = 0;

/* Function prototypes */
//unsigned long isqrt32(register unsigned long h);
int16_t dc_estimator(register int32_t *p, register int16_t x);
int16_t ir_filter(int16_t sample);
int16_t vs_filter(int16_t sample);
void set_LCD(void);
void display_number(int value, int start, int width);
void display_pulse(int on);
void display_correcting(int x, int on);

void main(void)
{
    double f1;
    int32_t x;
    int32_t y;    
    
    WDTCTL = WDTPW | WDTHOLD; 
    SCFI0 |= FN_4;                          // x2 DCO frequency, 8MHz nominal
                                            // DCO
    SCFQCTL = 91;                           // 32768 x 2 x (91 + 1) = 6.03 MHz
    FLL_CTL0 = DCOPLUS + XCAP14PF;          // DCO+ set so freq = xtal x D x
                                            //(N + 1)
    // Loop until 32kHz crystal stabilizes
    do
    {
      IFG1 &= ~OFIFG;                       // Clear oscillator fault flag
      for (j = 50000; j; j--);              // Delay
    }
    while (IFG1 & OFIFG);                   // Test osc fault flag
    
    // Setup GPIO
    P1DIR = 0xFF;
    P1OUT = 0;
    P2DIR = 0xFF;
    P2DIR |= BIT2 + BIT3;                   // P2.2 and P2.3 o/p direction - 
                                            // drives PNP transistors in H-Bridge
    P2OUT = 0;
    P3DIR = 0xFF;
    P3OUT = 0;
    P4DIR = 0xFF;
    P4OUT = 0;
    P5DIR = 0xFF;
    P5OUT = 0;
    P6OUT = 0; 
    
    /* Setup LCD */
    set_LCD(); 
    
    /* First amplifier stage - transconductance configuration */
    P6SEL |= (BIT0 | BIT1 | BIT2);          // Select OA0O
                                            // -ve=OA0I0, +ve=OA0I1
    OA0CTL0 = OAN_0 | OAP_1 | OAPM_3 | OAADC1;
    OA0CTL1 = 0;    
    
    /* Second amplifier stage */
    P6SEL |= (BIT3 | BIT4);                 // Select 0A1O 0A1I
                                            // -ve=OA1I0, +ve=DAC1
                                            // -ve=OA1I0, +ve=DAC1
//    OA1CTL0 = OAN_0 | OAP_3 | OAPM_3 | OAADC1;
//    OA1CTL1 = 0x00;   
                                            // Inverted input internally 
                                            // connected to OA0 output 
    OA1CTL0 = OAN_2 + OAP_3 + OAPM_3 + OAADC1;
    OA1CTL1 = OAFBR_7 + OAFC_6;             // OA as inv feedback amp, internal
                                            // gain = 15;    
    
    /* Configure DAC 1 to provide bias for the amplifier */
    P6SEL |= BIT7;
    DAC12_1CTL = DAC12CALON | DAC12IR | DAC12AMP_7 | DAC12ENC;
    DAC12_1DAT = 0; 
    
    /* Configure DAC 0 to provide variable drive to the LEDs */
    DAC12_0CTL =  DAC12CALON | DAC12IR | DAC12AMP_7 | DAC12ENC; // VRef+, high speed/current, 
                                            // DAC12OPS=0 => DAC12_0 output on P6.6 (pin 5) */
                                            // Configure P2.2 and P2.3 to 
                                            // provide variable drive to LEDs
    P2OUT |= BIT2;                          // turn off source for D2
    P2OUT &= ~BIT3;                         // turn on source for D3        
    DAC12_0DAT = 3340;    

                                            // Set initial values for the LED brightnesses 
    ir_LED_level = 1300;
    vs_LED_level = 1450;    
    
    /* Configure ADC12 */
    ADC12CTL0 &= ~ENC;                      // Enable conversions
                                            // Turn on the ADC12, and
                                            // set the sampling time
    ADC12CTL0 = ADC12ON + MSC + SHT0_4 + REFON + REF2_5V;
    ADC12CTL1 = SHP + SHS_1 + CONSEQ_1;     // Use sampling timer, single sequence,
                                            // TA1 trigger(SHS_1), start with ADC12MEM0
    ADC12MCTL0 = INCH_1 + SREF_1;           // ref+=Vref, channel = A1 = OA0
    ADC12MCTL1 = INCH_3 + SREF_1 + EOS;     // ref+=Vref, channel = A3 = OA1
    ADC12IE = BIT1;                         // ADC12MEM1 interrupt enable
    ADC12CTL0 |= ENC;                       // Enable the ADC
    ADC12CTL0 |= ADC12SC;                   // Start conversion    
    
    /* Configure Timer */
    TACTL = TASSEL0 + TACLR;                // ACLK, clear TAR,
    TACCTL1 = OUTMOD_2;
    TACCTL0 = CCIE;
                                            // This gives a sampling rate of
                                            // 512sps
    TACCR0 = 31;                            // Do two channels, at
                                            // 512sps each.
    TACCR1 = 10;                            // Allow plenty of time for the
                                            // signal to become stable before
                                            // sampling   
    TACTL |= MC_1;                          // Timer A on, up mode     
                                            
    /*Configure USART, so we can report readings to a PC */
    P2DIR |= BIT4;
    P2SEL |= BIT4;
    
    UCTL0 |= SWRST;
    ME1 |= UTXE0;                           // Enable USART1 TXD
    UCTL0 |= CHAR;                          // 8-bit char, SWRST=1
    UTCTL0 |= SSEL1;                        // UCLK = SMCLK
    UBR00 = 52;                             // 115200 from 6.02MHz = 52.33
    UBR10 = 0x00;
    UMCTL0 = 0x45;                          // Modulation = 0.375
    UCTL0 &= ~SWRST;                        // Initialise USART    
   
    while(1) 
    {
        __bis_SR_register(LPM0_bits + GIE); 
 
        /* Heart Rate Computation */
        f1 = 60.0*512.0*3.0/(float)log_heart_signal_sample_counter;
        heart_rate = f1;
        display_number(heart_rate, 3, 3);
        heart_rate_LSB = heart_rate & 0x00FF;
        
        /* SaO2 Computation */
        x = log_sq_ir_heart_ac_signal/log_heart_signal_sample_counter;
        y = log_sq_vs_heart_ac_signal/log_heart_signal_sample_counter;
        Ratio = (unsigned int) (100.0*log(y)/log(x));
        if (Ratio > 66)
          SaO2 = Lookup[Ratio - 66];        // Ratio - 50 (Look-up Table Offset) - 16 (Ratio offset)
        else if (Ratio > 50)
          SaO2 = Lookup[Ratio - 50];        // Ratio - 50 (Look-up Table Offset)
        else
          SaO2 = 100;
        display_number(SaO2, 7, 3); 
        SaO2_LSB = SaO2 & 0x00FF;
    }
}
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

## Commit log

2014-05-31 first version of @Kliment 's PCB
2014-06-06 Add design files
    [pulseoxrecv.brd, pulseoxrecv.sch]
2014-06-30 A folder to keep current documentation
2014-07-14 Add stm32f0-based pulse ox with new receiver module
    [pulseoxintegr.brd, pulseoxintegr.sch]
2014-07-15 move a silkscreen layer off one of the inductor pads
    [pulseoxintegr.brd]
2015-06-13 first prototype of finger clamp
2015-06-13 made top part finger channel much wider
2015-06-13 Changed Readme to be more reasonable. Added introduction and current status
2015-06-14 made the pcb cuts deeper
    [Clamp_output.stl]
2016-05-04 Add Ethics board recommendation and response for resubmission
2016-08-04 Add publication draft with introduction and calibration methods
2017-03-14 Allow for toner transfer creation of board
2017-03-14 Change case to fit lower-case naming convention
2017-03-14 Move old version to archive directory
    [pulseox-v1.brd, pulseox-v1.sch]
2017-03-14 Update Bill of Materials
    [bill_of_materials.ods]
2017-03-14 Update PCB images to V2 board design
2017-03-15 First complete draft of PCB for etching
    [pcb calculator.ods]
2018-07-21 Rename to more reasonable name
    [pulseoxintegr.brd, pulseoxintegr.sch]
2018-08-08 Renamed pulseox boards
    [pulseox.brd, pulseox.sch]
2018-10-08 Move over 2016-05-04 material
2019-06-25 Change to current version of pulse oximeter (IRNAS version) and create all parts as submodules
    [Clamp_output.stl, bill_of_materials.ods, pcb calculator.ods, pulseox-v1.brd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]
2019-06-25 Updated README to reflect current status of repo
2019-10-05 Add Case report form
2019-10-05 Update Case Report Form
